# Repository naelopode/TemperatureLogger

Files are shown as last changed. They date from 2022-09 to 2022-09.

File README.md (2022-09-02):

# Temperature Logger


This projet was realized during two mandatory civil services for the RISK group of the the institute of earth sciences (ISTE) of Lausanne University (UNIL) in 2021 and 2022.

The goal is to measure temperatures at different depths in a rock for several months. With this version we can log up to 6 external temperature sensors and one internal temperature sensor and log this data on an SD card. The logger should be able to run for several months outside.

# Containing
1. Arduino Code
2. Fritzing file
3. Gerber and PDF file of the custom PCB

# Capture data example


# Material
| Part                                               | Quantity |
|----------------------------------------------------|----------|
| Adafruit Feather M0 Adalogger                      | 1        |
| Adafruit MAX31865 PT1000                           | 5        |
| Adafruit DS3231 Precision RTC Breakout             | 1        |
| Platinum RTD Sensor - PT1000 - 3 Wire 1 meter long | 5        |
| 1-Wire DS18B20                                     | 1        |
| Solar Panel                                        | 1        |
| 5V Buck Converter Unit(ME3116AM6G)                 | 1        |
| USB / DC / Solar Lithium Ion/Polymer charger       | 1        |
| 4.7k Ohm Resistor                                  | 1        |
| Waterproof-Box                                     | 1        |
| 3-Pin IP67 Connector (for the Temperature sensors) | 6        |
| 2-Pin IP67 Connector (for the solar Panel)         | 1        |
| Micro-SD card                                      | 1        |
| Custom PCB                                         | 1        |

# Library Used
|   Library   |  Version  |
|-------------|-----------|
|[RTCZero.h](https://www.arduino.cc/reference/en/libraries/rtczero/)|1.6.0|
|[DS3231.h](https://www.arduino.cc/reference/en/libraries/ds3231/)|1.1.0|
|[Wire.h](https://github.com/esp8266/Arduino/blob/master/libraries/Wire/Wire.h)|1.0.0|
|[Adafruit_MAX31865.h](https://github.com/adafruit/Adafruit_MAX31865)|1.5.0|
|[DS3232RTC.h](https://github.com/JChristensen/DS3232RTC)|2.0.1|
|[DallasTemperature.h](https://github.com/milesburton/Arduino-Temperature-Control-Library)|3.9.0|
|[Onewire.h](https://www.arduino.cc/reference/en/libraries/onewire/)|2.3.7|
|[SD.h](https://www.arduino.cc/reference/en/libraries/sd/)|1.2.4|
|[SPI.h](https://www.arduino.cc/reference/en/language/functions/communication/spi/)|1.7.10|
# Board package
You also need the additional board package for the Adafruit SAMD Boards.
## In Visual Studio Code:
1. Install Arduino in the extension tab
2. With _control+shift+p_ write _>Arduino: Board Manager_
3. Click _Additional URLs_ and add 
> https://adafruit.github.io/arduino-board-index/package_adafruit_index.json
4. With _control+shift+p_ write _>Arduino: Board Config_
5. As board select: __Adafruit Feather M0 (SAMD21) (Adafruit SAMD Boards)_

## In Arduino IDE:
1. Open _Preferences_
2. In _Additional Boards Manager URLs_ add:
> https://adafruit.github.io/arduino-board-index/package_adafruit_index.json
3. In _tools_ > _Card type_ > _Adafruit Feather M0 (SAMD21)_ 

# Circuit
A friting file is available and a PCB can be produced from the file.
|Circuit                    |Schematic                      |PCB                 |
|---------------------------|-------------------------------|--------------------|
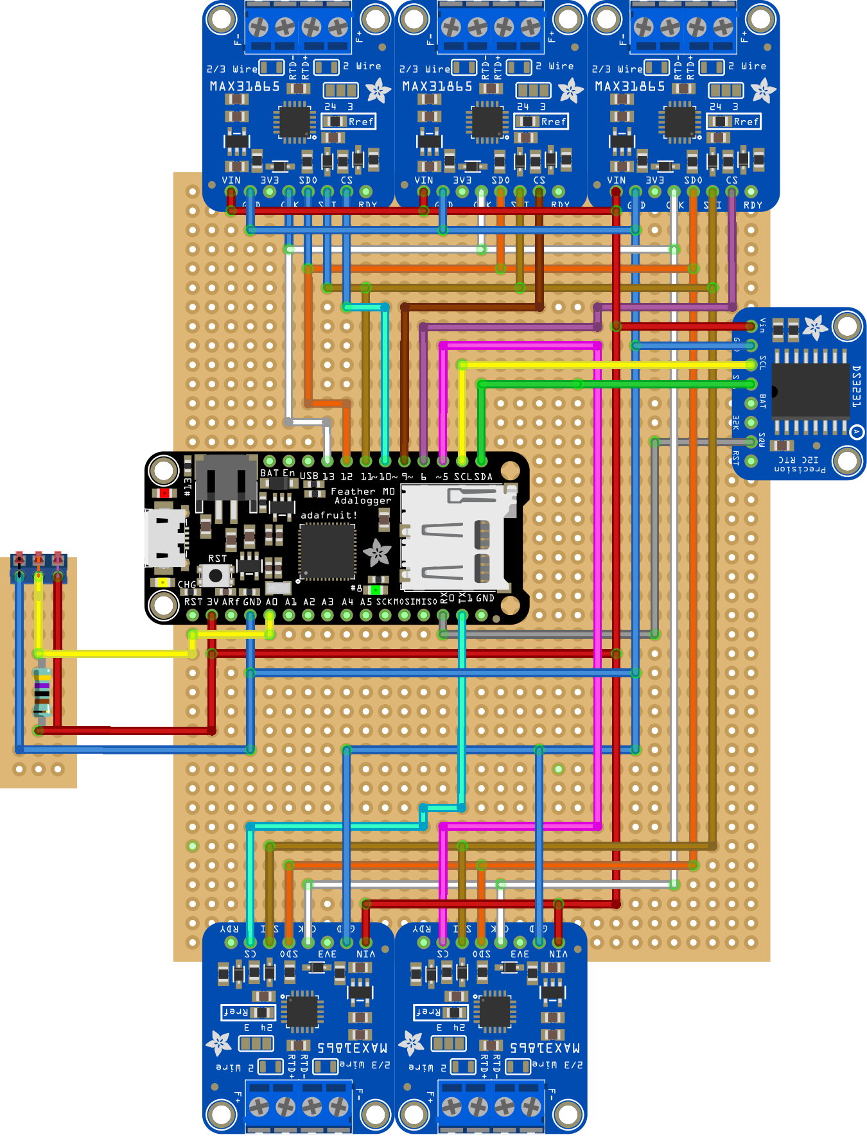
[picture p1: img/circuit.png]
Circuit
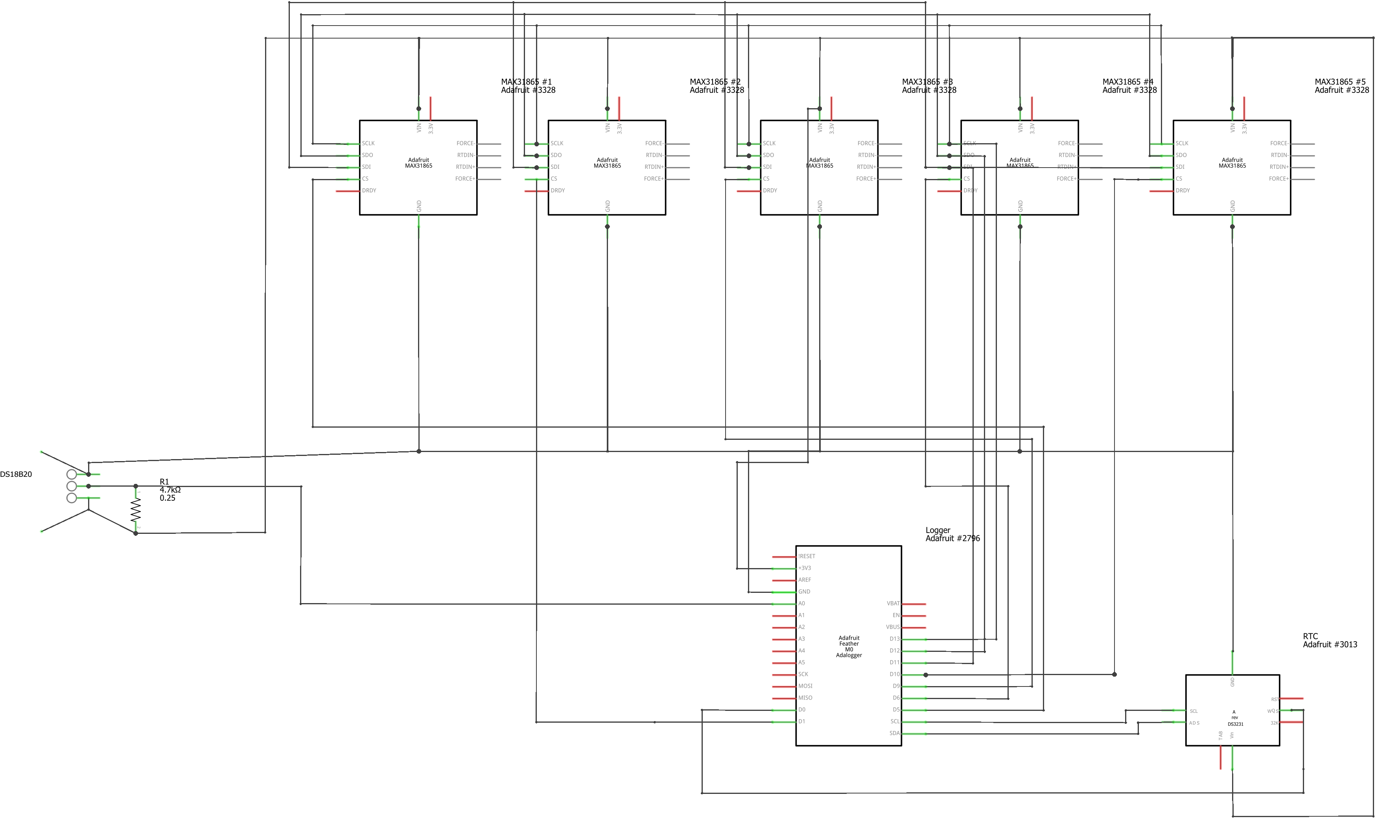
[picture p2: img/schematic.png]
Schematic
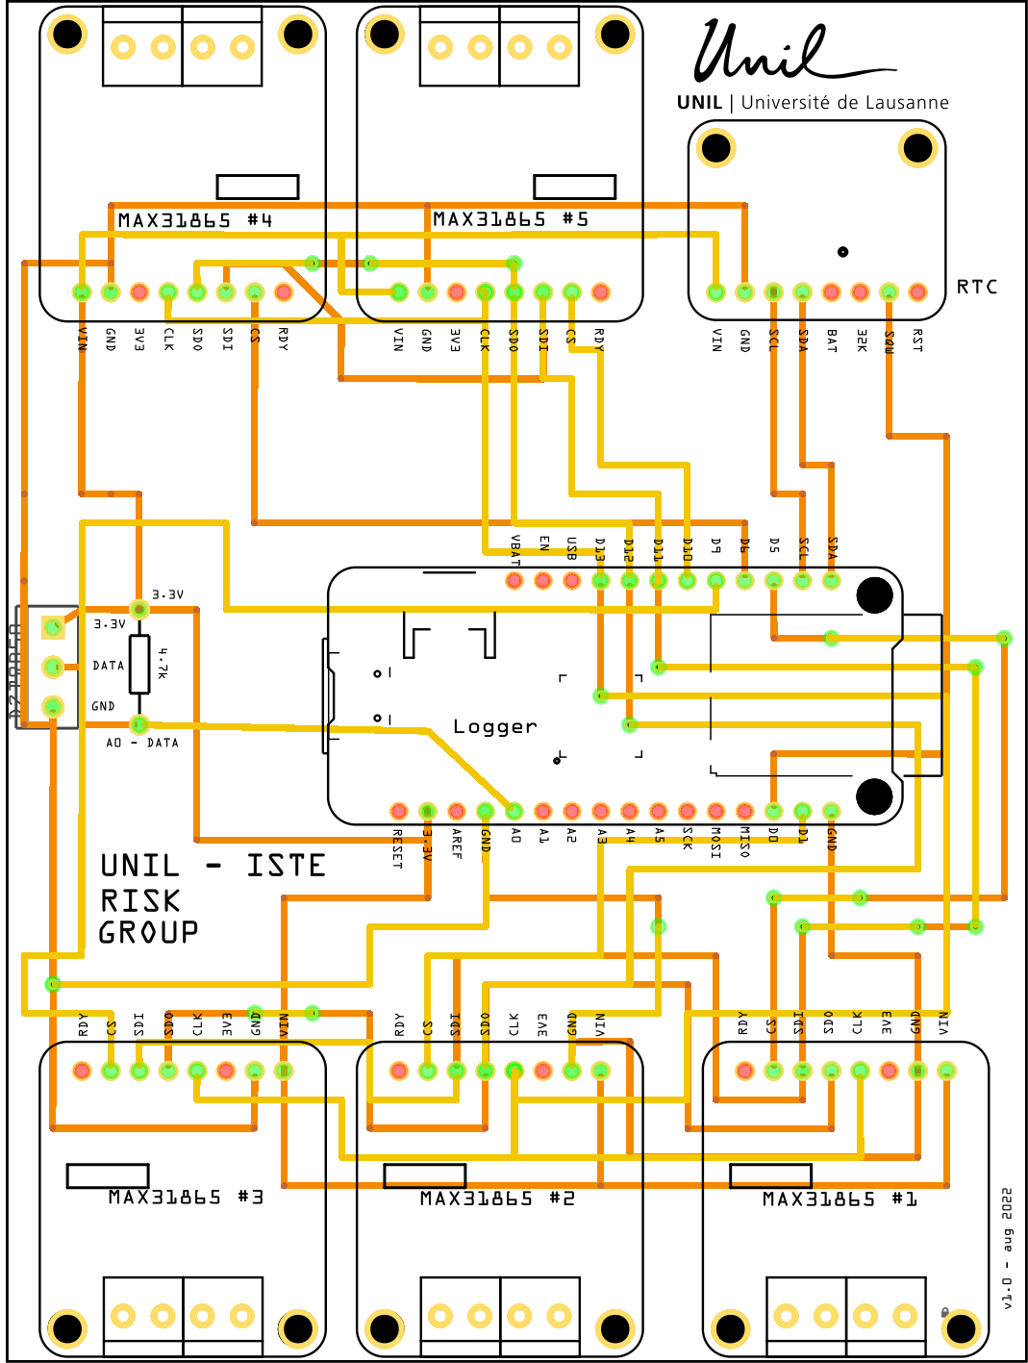
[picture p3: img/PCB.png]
PCB
||||

# Ports configuration
| Feather M0 Port        | Corresponding Port        | Feather M0 Port        | Corresponding Port        |
|------------------------|---------------------------|------------------------|---------------------------|
| D0                     | RTC DS3231 (SQW)          | D12                    | MAX31865 #1-#5 (SDO)      |
| D1                     | MAX31865 #2 (CS)          | D13                    | MAX31865 #1-#5 (CLK)      |
| D5                     | MAX31865 #1 (CS)          | A0                     | DS18B20 (DATA)            |
| D6                     | MAX31865 #4 (CS)          | SCL                    | RTC DS3131 (SCL)          |
| D9                     | MAX31865 #3 (CS)          | SDA                    | RTC DS3131 (SCA)          |
| D10                    | MAX31865 #5 (CS)          | 3.3V                   | All Vin ports             |
| D11                    | MAX31865 #1-#5 (SDI)      | GND                    | All GND ports             |

# Parameters
The main parameters are declared at the start of LowPowerLogger.ino
> _SampleIntSec_: Define the sampling interval (Default: 60) \
> _SamplesPerCycle_: Define after how many samples we flush the log (as flushing once per sampling wouldn't be too consuming) (Default: 10)\
>_NUM_MAX31865_: Number of MAX31865 (Default: 5)\
>_RREF1...5_: Default reference resistor value of MAX31865 (Default: 4300)\
>_RNOMINAL_: Default nominal resistor value of MAX31865 (Default: 1000)\
>_AVERAGE_MEASURES_: Number of measures taken form MAX31865 averaged for one measure (Default: 10)\

# Usage
Always unplug the 2-pin JST connector from the USB/DC/Solar Lithium Ion/Polymer charger before plugging-in a __micro-USB__  cable.
## Standalone (Only writing on the SD card)
Download LowPowerLogger.ino on the Arduino with line 11 commented.
>_//#define ECHO_TO_SERIAL_
1. Unconnect the micro-usb
2. Plug-in the micro-SD card
3. Plug-in the 2-pin JST connector from the USB/DC/Solar Lithium Ion/Polymer 
If you remove the micro-SD card while the battery is plugged in, remember to push the reset button of the Arduino once the micro-SD card is back in.

## With a computer (Writing on the SD card and Serial)
Uncomment the line 11 of LowPowerLogger.ino
>_#define ECHO_TO_SERIAL_

And setup the serial monitor to the baude rate of 115200
Do not plug in the JST connector to the USB/DC/Solar Lithium Ion/Polymer charger

## Recharching battery
Use a __mini-USB__ cable, pluged-in the USB/DC/Solar Lithium Ion/Polymer charger to recharge the battery.

## Important notice
**Never connect the micro-USB cable to the board if the USB/DC/Solar Lithium Ion/Polymer charger JST Connector is plugged in as the module does not have a protection diode.**

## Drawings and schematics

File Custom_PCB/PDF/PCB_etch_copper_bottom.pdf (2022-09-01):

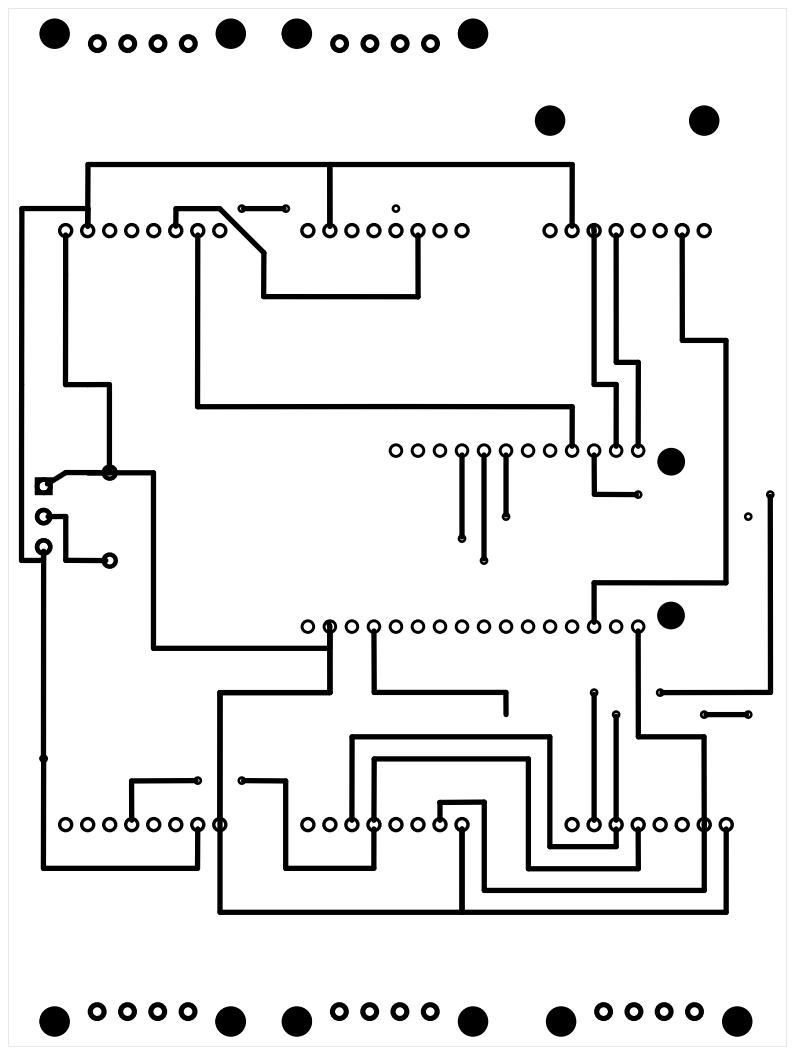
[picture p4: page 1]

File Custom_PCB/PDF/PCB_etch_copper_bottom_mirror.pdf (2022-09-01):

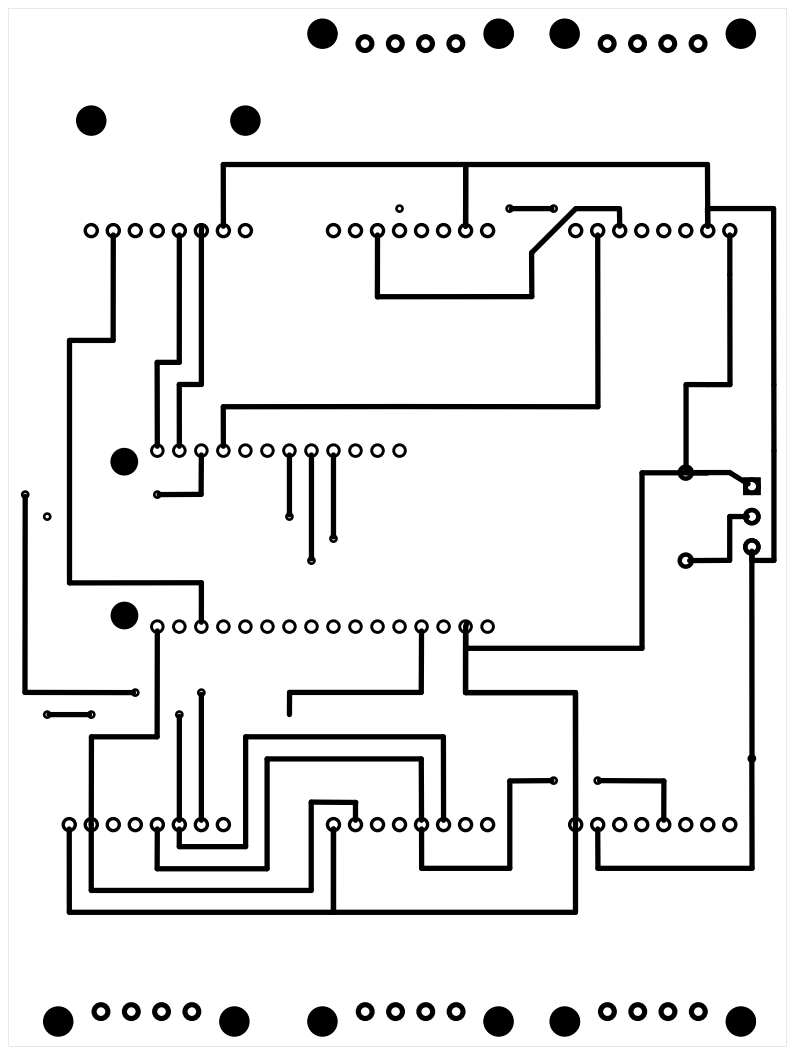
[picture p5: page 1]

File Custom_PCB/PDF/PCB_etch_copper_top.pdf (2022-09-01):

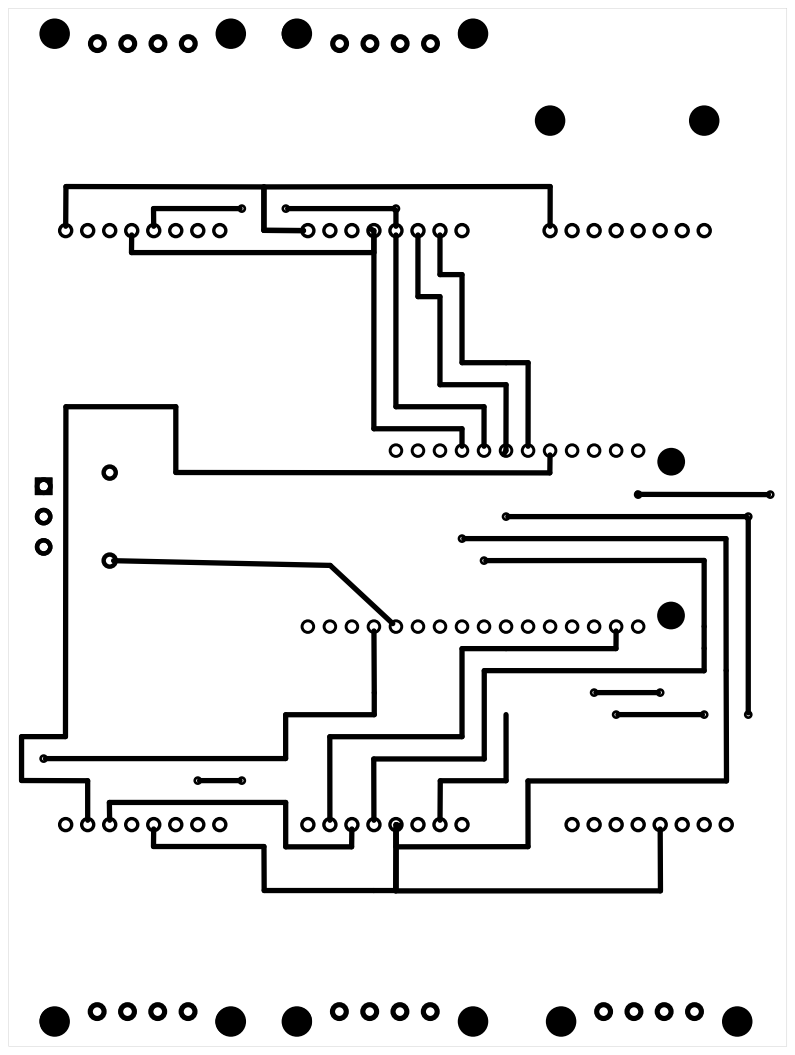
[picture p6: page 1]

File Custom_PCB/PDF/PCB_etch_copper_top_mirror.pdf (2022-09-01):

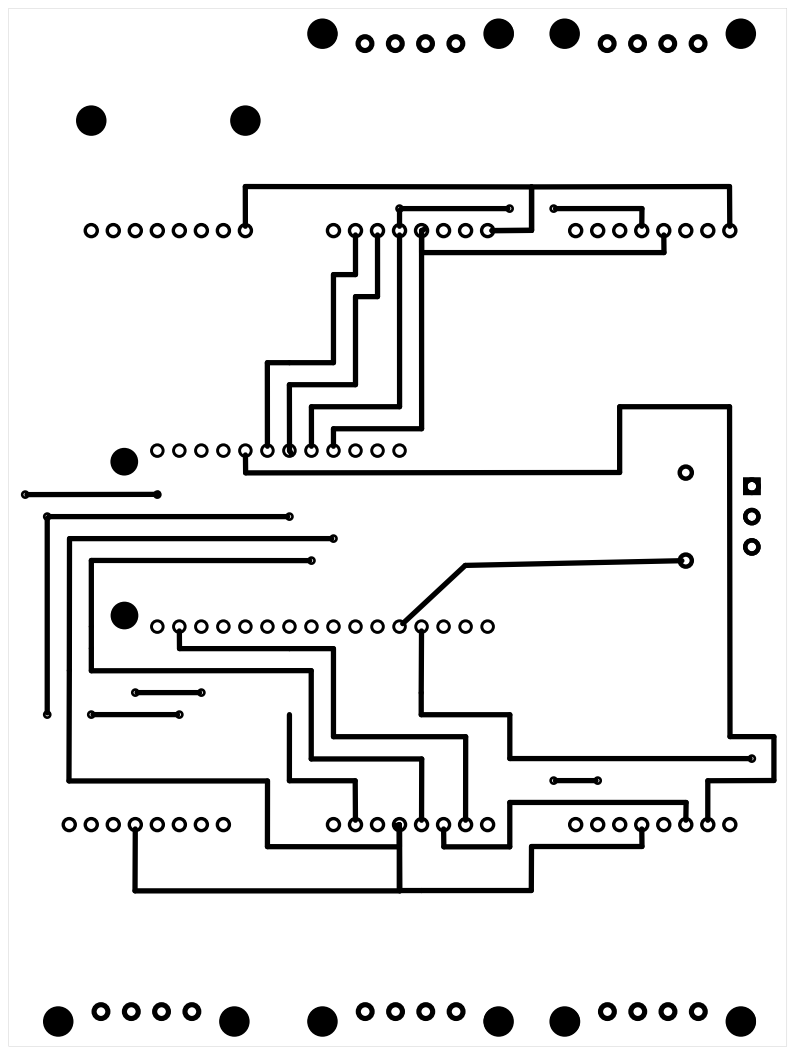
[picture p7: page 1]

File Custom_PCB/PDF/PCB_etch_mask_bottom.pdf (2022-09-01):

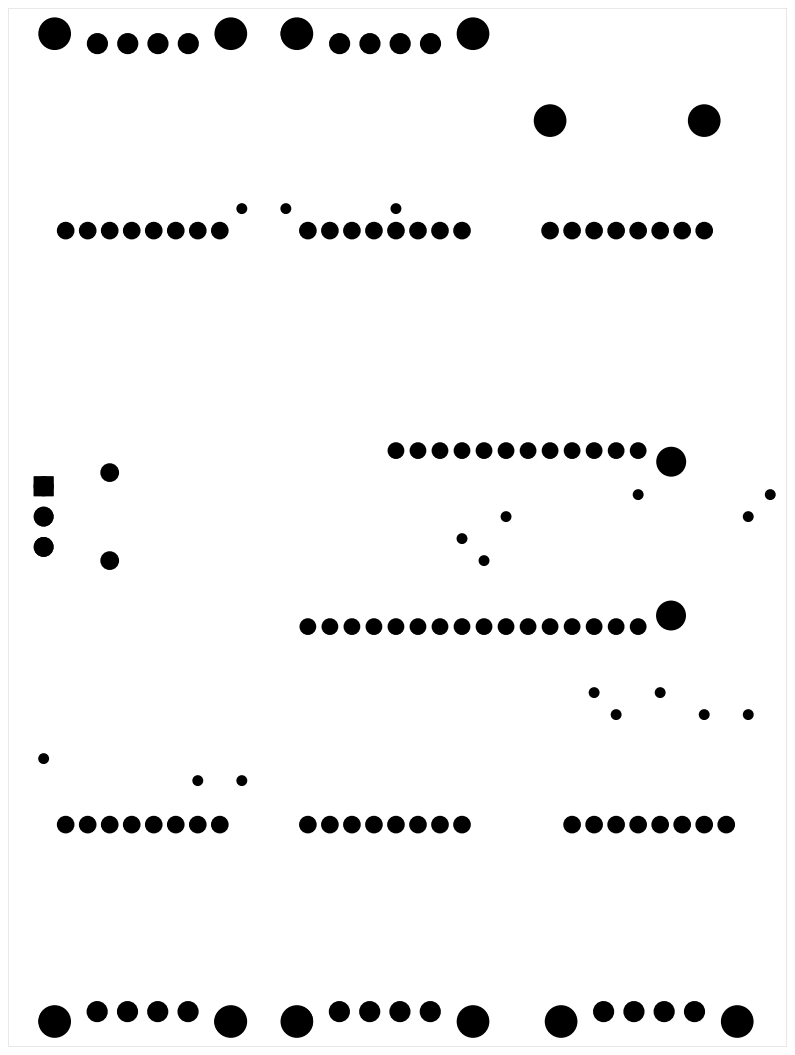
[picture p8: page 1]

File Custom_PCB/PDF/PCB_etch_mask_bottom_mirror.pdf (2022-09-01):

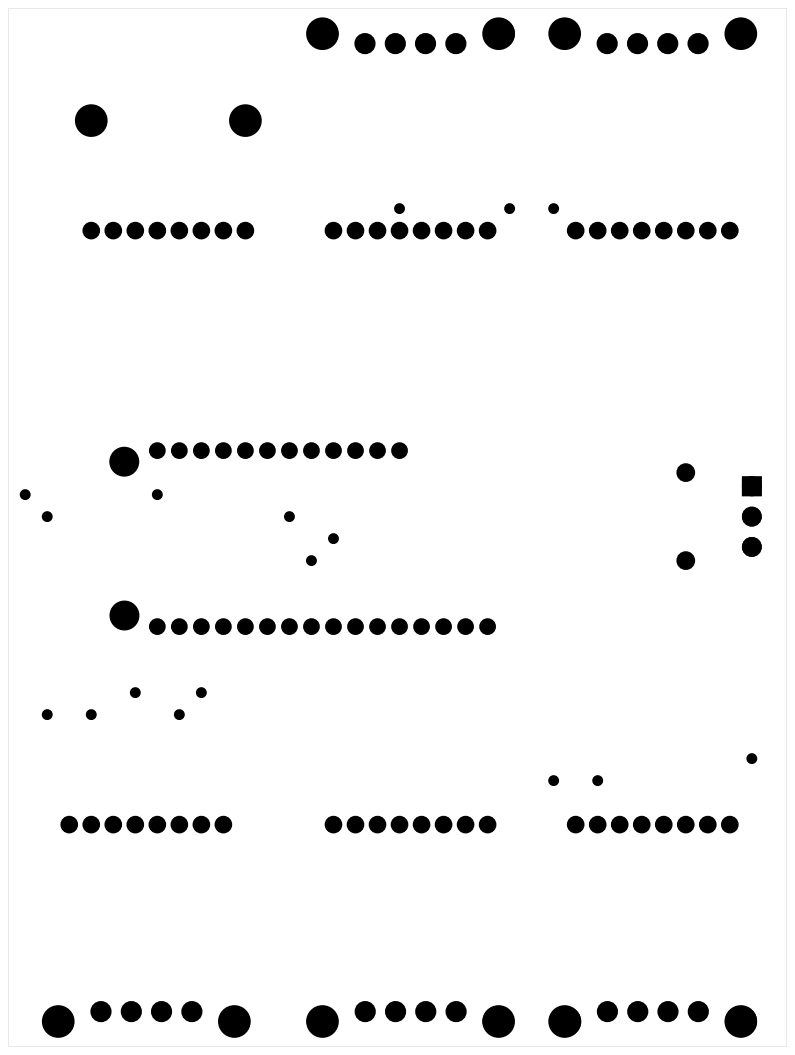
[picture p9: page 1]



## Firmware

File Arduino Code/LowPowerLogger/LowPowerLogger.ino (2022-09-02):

/*
 Low Power Temperature Logger for Feather M0 Adalogger
 Uses internal RTC and interrupts to put M0 into deep sleep, sync with external RTC.
 Uses 5 PT1000 with MAX31865, 1 DS18B20 with 4.7k Pull-Up Resistor, 1 on the DS3231 (inside the box)
 Output logged to uSD at intervals set
 Created in august 2022 for ISTE - UNIL - RISK GROUP
 Based on  cavemoa's code
*/

////////////////////////////////////////////////////////////
//#define ECHO_TO_SERIAL // Uncomment for serial output
////////////////////////////////////////////////////////////

#include <SPI.h>
#include <SD.h>
#include <RTCZero.h> 
#include <DS3231.h>
#include <Wire.h>
#include <Adafruit_MAX31865.h> 
#include <OneWire.h>
#include <DallasTemperature.h>


bool century = false;
bool h12Flag;
bool pmFlag;


#define cardSelect 4  // Set the pin used for uSD

//////////////// Key Settings ///////////////////

#define SampleIntSec 60 // RTC - Sample interval in seconds
#define SamplesPerCycle 10  // Number of samples to buffer before uSD card flush is called


// The value of the Rref resistor. Use optimisation prog to calculate
#define NUM_MAX31865 5    //Number of MAX31865 sensor
#define RREF1      4300.0
#define RREF2      4300.0 
#define RREF3      4300.0 
#define RREF4      4300.0 
#define RREF5      4300.0 
// The 'nominal' 0-degrees-C resistance of the sensor
#define RNOMINAL   1000.0

#define AVERAGE_MEASURES     10 //number of mesure take and averaged to take 1 better mesure

#define ONE_WIRE_BUS A0

// Setup a oneWire instance to communicate with any OneWire devices
OneWire oneWire(ONE_WIRE_BUS);

// Pass our oneWire reference to Dallas Temperature sensor 
DallasTemperature sensors(&oneWire);

//const int SampleIntSeconds = 2000;   //Simple Delay used for testing, ms i.e. 1000 = 1 sec DELETE

Adafruit_MAX31865 thermo5 = Adafruit_MAX31865(10, 11, 12, 13);
Adafruit_MAX31865 thermo3 = Adafruit_MAX31865(9, 11, 12, 13);
Adafruit_MAX31865 thermo4 = Adafruit_MAX31865(6, 11, 12, 13);
Adafruit_MAX31865 thermo1 = Adafruit_MAX31865(5, 11, 12, 13);
Adafruit_MAX31865 thermo2 = Adafruit_MAX31865(1, 11, 12, 13);



/////////////// Global Objects ////////////////////
RTCZero rtc;    // Create RTC object
File logfile;   // Create file object
float measuredvbat;   // Variable for battery voltage
int NextAlarmSec; // Variable to hold next alarm time in seconds
unsigned int CurrentCycleCount;  // Num of smaples in current cycle, before uSD flush call
DS3231 myRTC;   //Create external RTC object

//////////////    Setup   ///////////////////
void setup() {
  Wire.begin();   //Start 1Wire communication
  rtc.begin();    // Start the RTC in 24hr mode
  rtc.setTime(myRTC.getHour(h12Flag, pmFlag), myRTC.getMinute(), myRTC.getSecond());   // Set the time from external RTC
  rtc.setDate(myRTC.getDate(), myRTC.getMonth(century), myRTC.getYear());    // Set the date from external RTC
  WireStartup();  //Set MAX31865 as 3WIRE
  sensors.begin(); //Start for DS18B20
  #ifdef ECHO_TO_SERIAL
    while (! Serial); // Wait until Serial is ready
    Serial.begin(115200);
    Serial.println("\r\nFeather M0 Analog logger");
  #endif  

  // see if the card is present and can be initialized:
  if (!SD.begin(cardSelect)) {
    Serial.println("Card init. failed! or Card not present");
  }
  char filename[15];
  strcpy(filename, "ANALOG00.CSV");
  for (uint8_t i = 0; i < 100; i++) {
    filename[6] = '0' + i/10;
    filename[7] = '0' + i%10;
    // create if does not exist, do not open existing, write, sync after write
    if (! SD.exists(filename)) {
      break;
    }
  }

  logfile = SD.open(filename, FILE_WRITE);
  if( ! logfile ) {
    Serial.print("Couldnt create "); 
    Serial.println(filename);
  }
  Serial.print("Writing to "); 
  Serial.println(filename);

  Serial.println("Logging ....");
  writeHeader();
}

/////////////////////   Loop    //////////////////////
void loop() {

  CurrentCycleCount += 1;     //  Increment samples in current uSD flush cycle

  #ifdef ECHO_TO_SERIAL
    SerialOutput();           // Only logs to serial if ECHO_TO_SERIAL is uncommented at start of code
  #endif
  
  SdOutput();                 // Output to uSD card

  // Code to limit the number of power hungry writes to the uSD
  if( CurrentCycleCount >= SamplesPerCycle ) {
    logfile.flush();
    CurrentCycleCount = 0;
    #ifdef ECHO_TO_SERIAL
      Serial.println("logfile.flush() called");
    #endif
  }

  
  ///////// Interval Timing and Sleep Code ////////////////
  //delay(SampleIntSeconds);   // Simple delay for testing only interval set by const in header

  NextAlarmSec = (NextAlarmSec + SampleIntSec) % 60;   // i.e. 65 becomes 5
  rtc.setAlarmSeconds(NextAlarmSec); // RTC time to wake, currently seconds only
  rtc.enableAlarm(rtc.MATCH_SS); // Match seconds only
  delay(2); // Brief delay prior to sleeping not really sure its required
  
  rtc.standbyMode();    // Sleep until next alarm match
  
  // Code re-starts here after sleep !

}

///////////////   Functions   //////////////////

// Debbugging output of time/date and battery voltage
void SerialOutput() {
  sensors.requestTemperatures(); //request temps for DS18B20
  Serial.print(CurrentCycleCount);
  Serial.print(",");
  Serial.print(rtc.getDay());
  Serial.print("/");
  Serial.print(rtc.getMonth());
  Serial.print("/");
  Serial.print(rtc.getYear()+2000);
  Serial.print(" ");
  Serial.print(rtc.getHours());
  Serial.print(":");
  if(rtc.getMinutes() < 10)
    Serial.print('0');      // Trick to add leading zero for formatting
  Serial.print(rtc.getMinutes());
  Serial.print(":");
  if(rtc.getSeconds() < 10)
    Serial.print('0');      // Trick to add leading zero for formatting
  Serial.print(rtc.getSeconds());
  for (int i(0); i<NUM_MAX31865; ++i){
    Serial.print(",");
    Serial.print(get_temp_moy(i, AVERAGE_MEASURES));
  }
  Serial.print(",");
  Serial.println(myRTC.getTemperature());
  Serial.print(",");
  Serial.println(sensors.getTempCByIndex(0));
}

// Print data and time followed by battery voltage to SD card
void SdOutput() {
  sensors.requestTemperatures(); //request temps for DS18B20
  // Formatting for file output CycleCount, dd/mm/yyyy hh:mm:ss, [sensors output] x7
  logfile.print(CurrentCycleCount);
  logfile.print(",");
  logfile.print(rtc.getDay());
  logfile.print("/");
  logfile.print(rtc.getMonth());
  logfile.print("/");
  logfile.print(rtc.getYear()+2000);
  logfile.print(" ");
  logfile.print(rtc.getHours());
  logfile.print(":");
  if(rtc.getMinutes() < 10)
    logfile.print('0');      // Trick to add leading zero for formatting
  logfile.print(rtc.getMinutes());
  logfile.print(":");
  if(rtc.getSeconds() < 10)
    logfile.print('0');      // Trick to add leading zero for formatting
  logfile.print(rtc.getSeconds());
  for (int i(0); i<NUM_MAX31865; ++i){
    logfile.print(",");
    logfile.print(get_temp_moy(i, AVERAGE_MEASURES));
  }
  logfile.print(",");
  logfile.print(myRTC.getTemperature());
  logfile.print(",");
  logfile.print(sensors.getTempCByIndex(0));
  logfile.println();
}

// Write data header.
void writeHeader() {
  logfile.println("Cycle count,DD:MM:YYYY hh:mm:ss,T_SENSOR1,T_SENSOR2,T_SENSOR3,T_SENSOR4,T_SENSOR5,T_SENSOR_BOX,T_SENSOR_SURFACE");
}

void WireStartup() {
  thermo1.begin(MAX31865_3WIRE);  // set to 2WIRE or 4WIRE as necessary
  thermo2.begin(MAX31865_3WIRE);
  thermo3.begin(MAX31865_3WIRE);
  thermo4.begin(MAX31865_3WIRE);
  thermo5.begin(MAX31865_3WIRE);
}

double get_temp(int sensor) {
  switch (sensor) {
    case 0: return thermo1.temperature(RNOMINAL, RREF1);
    case 1: return thermo2.temperature(RNOMINAL, RREF2);
    case 2: return thermo3.temperature(RNOMINAL, RREF3);
    case 3: return thermo4.temperature(RNOMINAL, RREF4);
    case 4: return thermo5.temperature(RNOMINAL, RREF5); //You can add MAX31865 sensors here
  }
  return 0;
}

double get_temp_moy(int sensor, int nb) {
  double moyenne = 0;
  for (int i(0); i < nb; ++i) {
    moyenne += get_temp(sensor);
  }
  return (moyenne / nb);
}

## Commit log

2022-09-01 Add PCB Production file
    Everything needed to produce the custom PCB
    [PCB.gtl, PCB.gts, PCB_contour.gm1, PCB_copperBottom.gbl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]
2022-09-01 Add Fritzing file
    [Circuit.fzz]
2022-09-02 Add Arduino code
